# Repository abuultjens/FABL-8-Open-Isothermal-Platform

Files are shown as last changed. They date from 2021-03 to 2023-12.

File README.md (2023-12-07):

# FABL-8-Open-Isothermal-Platform
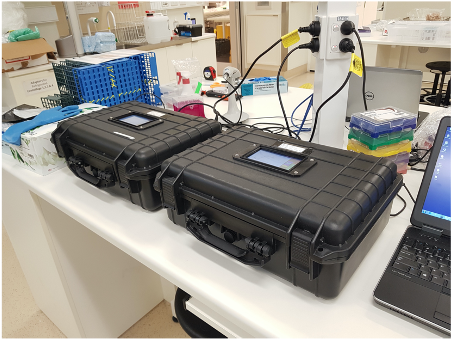
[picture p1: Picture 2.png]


Publicly accessible details on how to build and operate a FABL-8 isothermal diagnostic device. The build instructions have been divided into an essential and optional section. The essential section details how to build just the control, heating, excitation and emission systems as well as a touchscreen interface - the bare minimum for an operating isothermal diagnostic platform. The optional section describes how we built a casing for the instrument, however this specific design was not mandatory for function and could be used as a guide as there is considerable flexibility.

## About
The FABL-8 is an open source, low cost and scalable diagnostic platform for the running and monitoring of loop mediated isothermal amplification (LAMP) reactions. 

## Publication
A research article detailing the FABL-8 and its diagnostic performance against commercial offerings has been published in ACS Biomaterials Science & Engineering (DOI: 10.1021/acsbiomaterials.1c01105):
https://pubs.acs.org/doi/10.1021/acsbiomaterials.1c01105

## Video of instrument in operation
FABL-8 (https://youtu.be/c5SjP3wax4s "FABL-8 isothermal diagnostic platform")

## File download link
https://unimelbcloud-my.sharepoint.com/:f:/r/personal/buultjensa_unimelb_edu_au/Documents/FABL-8_files?csf=1&web=1&e=TzOEO4

## Page index
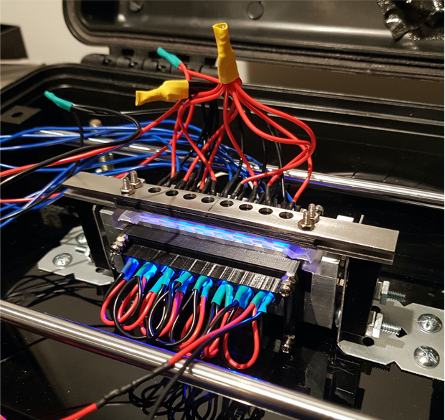
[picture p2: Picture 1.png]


- [Essential build](#essential-build)
  - [Electronic configuration](#electronic-configuration)  
    - [Circuit schematic](#circuit-schematic)
    - [Power source](#power-source)
    - [Setting up the Raspberry pi](#Setting-up-the-Raspberry-pi)
  - [Heating block](#heating-block)
  - [Heating block stands](#heating-block-stands)
  - [3D printed parts](#3d-printed-parts)
    - [Magnet mount](#magnet-mount)
    - [Fixed photodiode mount](#fixed-photodiode-mount)
    - [Fixed LED mount ](#fixed-led-mount)
  - [Assembly](#sssembly)
    - [Block stands and magnet mount](#block-stands-and-magnet-mount)
    - [Excitation system](#excitation-system)
    - [Emission system](#emission-system)
- [Instrument case](#instrument-case)
  - [3D printed parts](#3d-printed-parts)
    - [Left screen mount](#left-screen-mount)
    - [Right screen mount](#right-screen-mount)
    - [Screen face plate](#screen-face-plate)
  - [Block mounting partition](#block-mounting-partition)
- [Instructions of use](#instructions-of-use)
- [Essential build parts list](#essential-build-parts-list)
- [Instrument case parts list](#Instrument-case-parts-list)
- [Script index](#script-index)

# Essential build
This section details how to build just the control, heating, excitation and emission systems as well as a touchscreen interface - the bare minimum for an operating isothermal platform. All required parts can be found in the [Essential build parts list](#essential-build-parts-list).

## Electronic configuration
The circuit consists of five main systems:  
* __Voltage regulation__  
Provide individual step down 5V DC power supplies from the input 19V DC for the control, heater, excitation and emission systems. 
* __Control__  
Consists of a Raspberry pi that orchestrates the heater, excitation and emission systems. The control system uses a 12-stage binary counter to accurately  quantify the clock pulses from the emission system.  
* __Heater__  
Provides high current on/off switching of two 10W wire wound resistors that form the heating element. The heating system utilises a thermal breaker that acts as a failsafe to shutoff the heating element in the event of a control malfunction.
* __Excitation__  
Sequentially illuminates LEDs in an eight LED array using an 8-channel analogue multiplexer.
* __Emission__  
Sequentially reads clock pulses from light-to-frequency photodiodes in an eight photodiode array using an 8-channel analogue demultiplexer.    

Return to [page index](#page-index).

### Circuit schematic  
Note that the thin and thick lines indicate signal wires (current rating: 0.6A) and high current wires (current rating: 7.5A), respectively. 
Image description

Return to [page index](#page-index).

### Power source
We used 19V 6.3A laptop power supply packs as power sources for the FABLE-8 units. Alternatively, a 12V power pack with at least 10A output (120W) would suffice. Using a power supply with a different wattage may cause a different heating profile and the PID parameters may need to be slightly adjusted.

### Setting up the Raspberry pi  

1. Use SDFormatter (https://www.sdcard.org/downloads/) to perform a quick format of a microSD card.  

2. Download the preconfigured image from this page https://cloudstor.aarnet.edu.au/plus/s/Bz4BOmHrPozpWsq.
  
3. Use Raspberry Pi Imager (https://www.raspberrypi.org/software/) to write 'FABL-8_img.img.gz' image to a microSD card.  

Details of all scripts packaged into the image file can be found in the [Script index](#script-index).

Return to [page index](#page-index).

## Heating block
The heating block was made from solid aluminium  using a computer numerical control (CNC) machine. The lid plates and resistor retainer plates were made using a drill press. All 2.5mm holes in the heating block were tapped with metric 3mm (M3) threads.
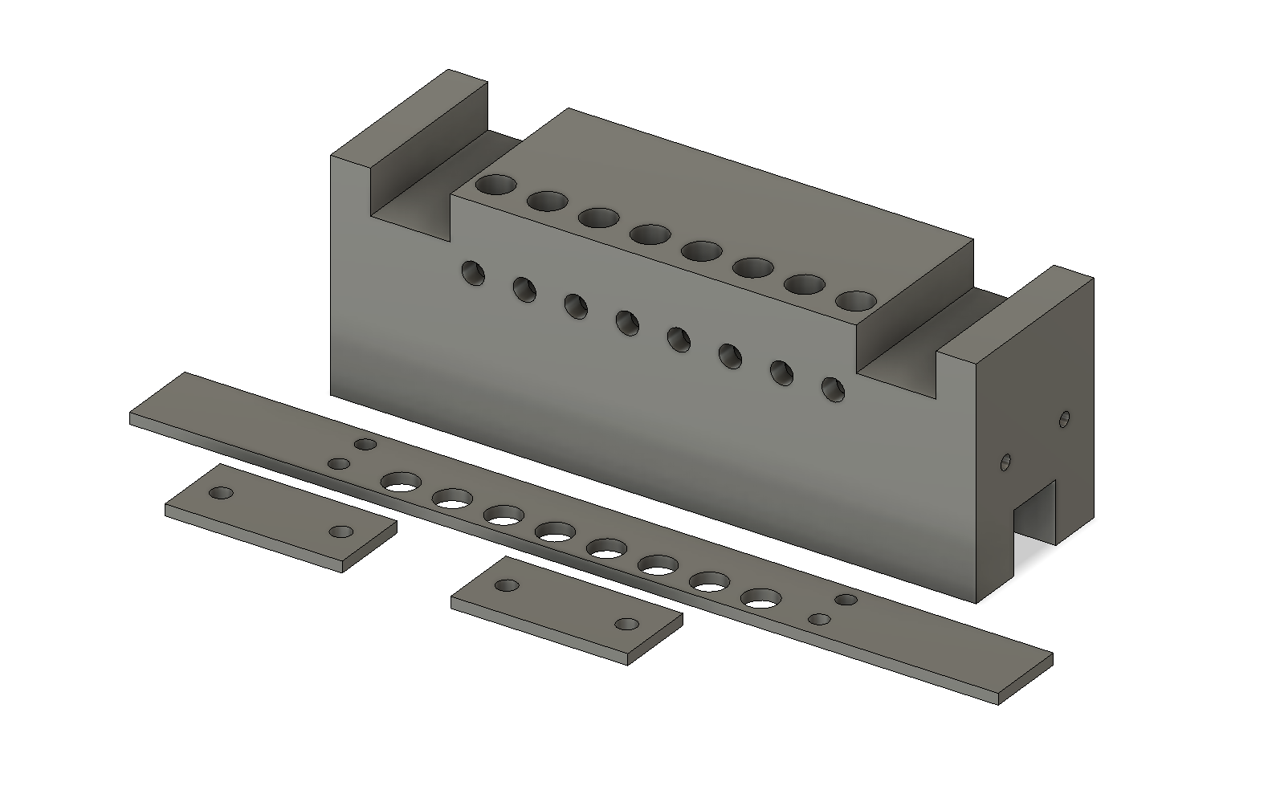
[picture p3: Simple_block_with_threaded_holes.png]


The thermal breaker and temperature sensor are mounted on the rear of the heating block. The thermal breaker mounts using M3 bolts while the temperature sensor is retained using a small clip made from sheet metal that is secured under a thermal breaker mounting bolt head.
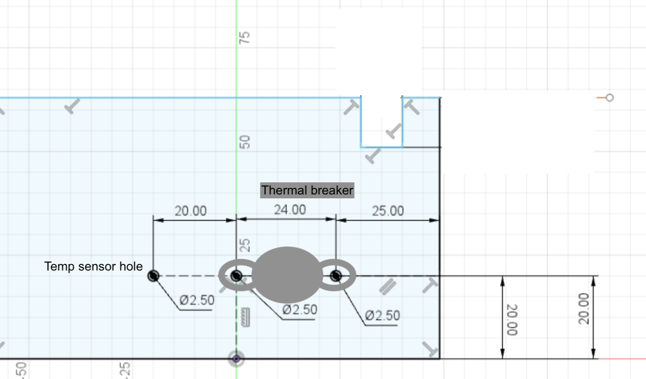
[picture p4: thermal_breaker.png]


Return to [page index](#page-index).

## Heating block stands
Stands were made from 1mm thick sheet metal. If sheet metal is difficult to source or work with, any kind of block mounting stand could be fabricated as long as it can withstand a constant 65oC.
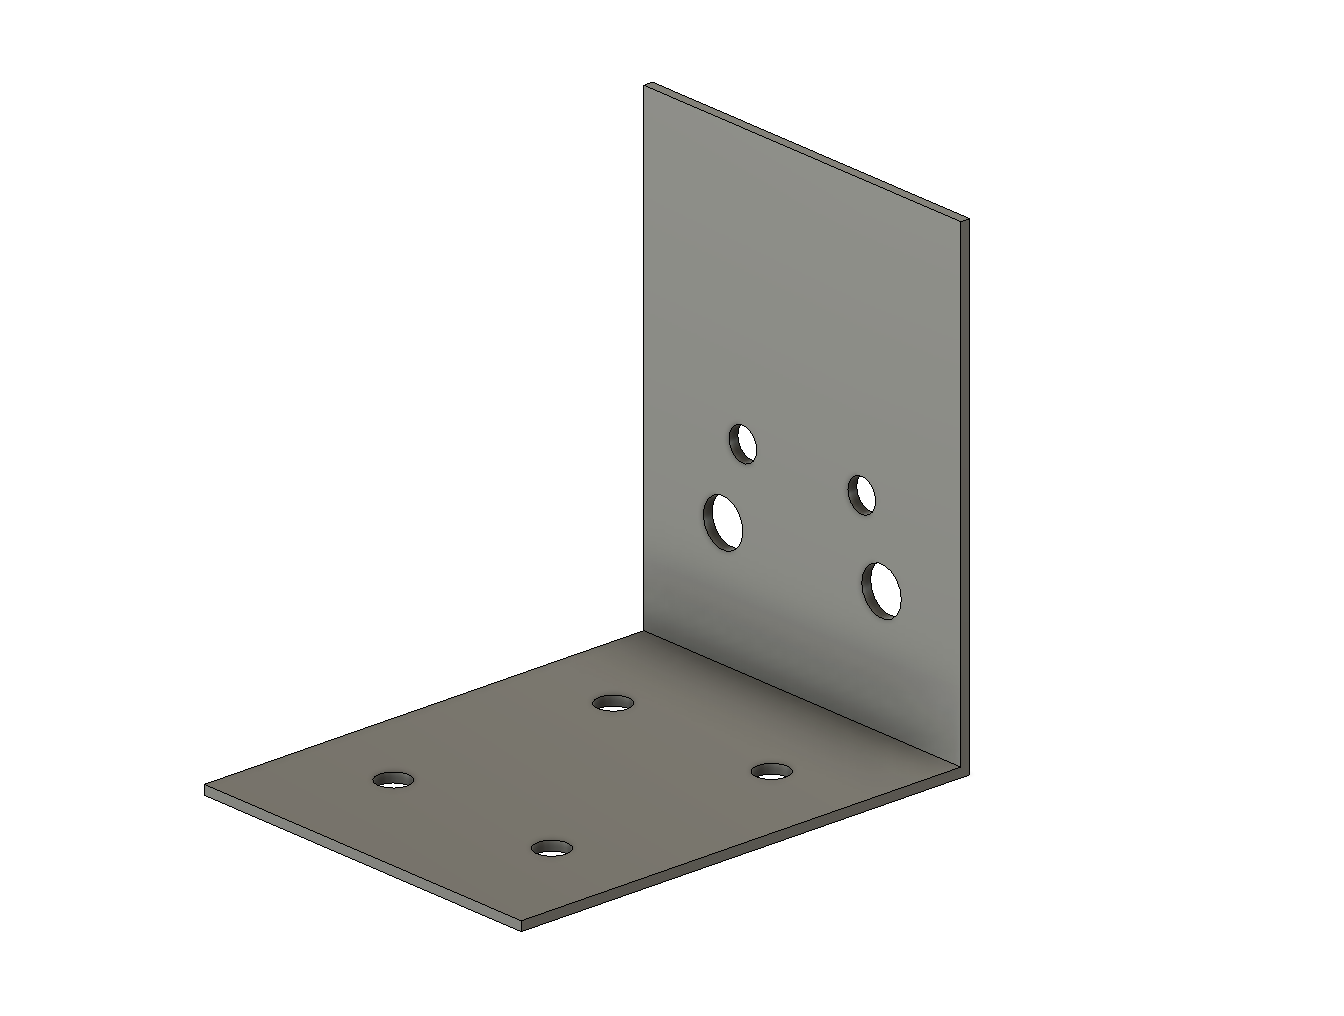
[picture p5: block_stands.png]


Return to [page index](#page-index).

## 3D printed parts
All 3D printed parts were printed using black 1.75 PLA filament on a Creality3D Ender-3 3D printer modified with a BLTouch V2 automatic mechanical bed levelling device (https://www.antclabs.com/bltouch).  

### Magnet mount  
Retains two rare earth magnets in its upper cavity. The mount holds the magnets captive when the closed end of the cavity is facing away from the block.
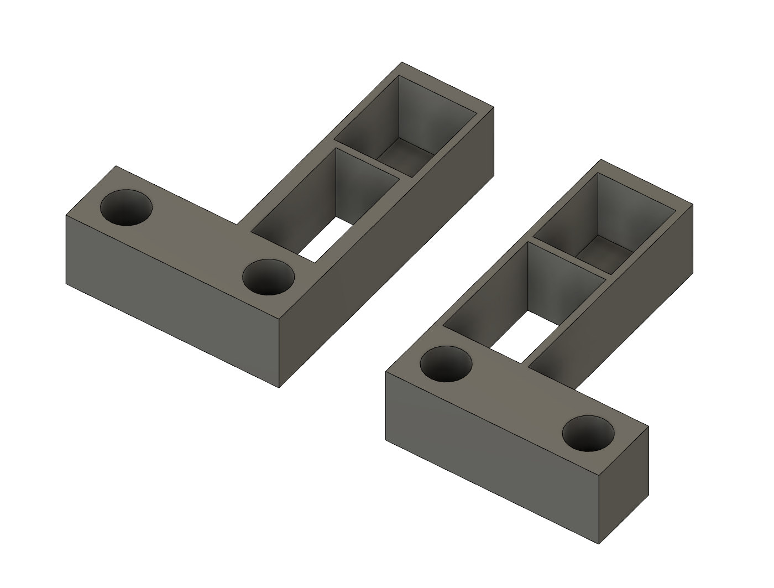
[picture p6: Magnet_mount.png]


Return to [page index](#page-index).

### Fixed photodiode mount  
Retains the eight photodiodes and is sandwiched between two 2mm thick block lid plates. The emission filter gel is mounted between the photodiodes and the lower block lid plate.
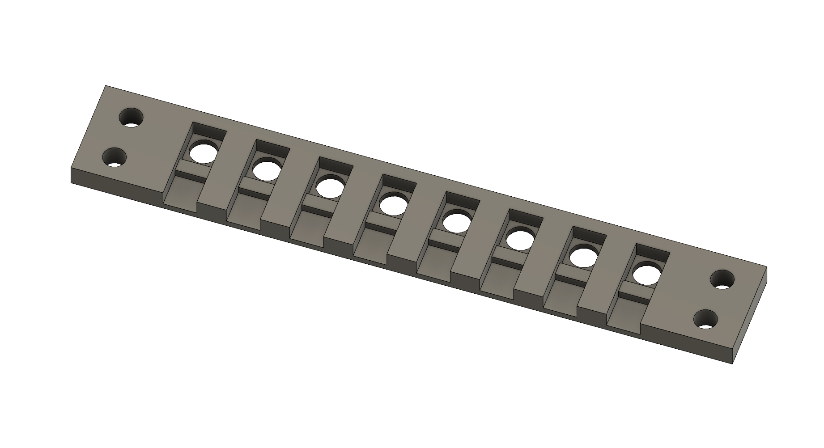
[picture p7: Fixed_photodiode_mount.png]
  

Return to [page index](#page-index).

### Fixed LED mount  
Retains the eight LEDs and clamps the excitation filter gel to the block.
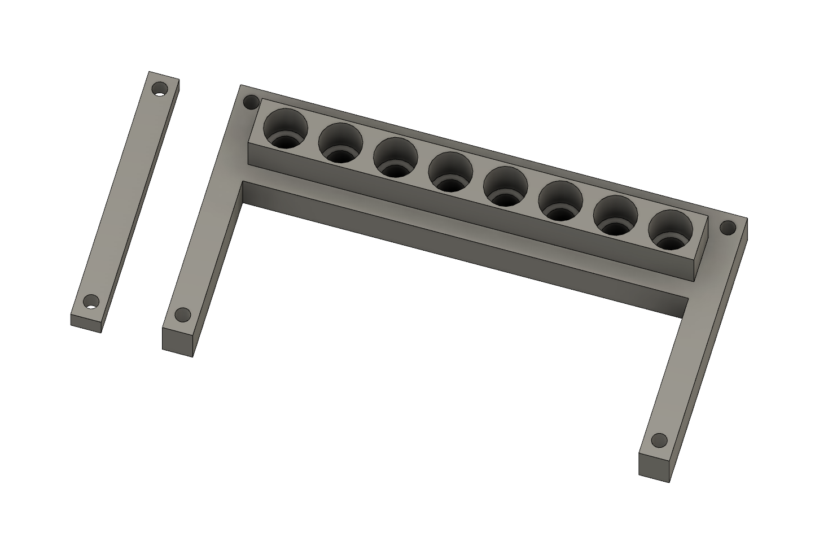
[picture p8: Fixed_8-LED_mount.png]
  

Return to [page index](#page-index).

## Assembly

### Block stands and magnet mount
Two wire wound resistors are fitted into the cavity underneath the heating block and are secured in place using the two resistor retaining plates. The magnet mount is first attached to the block stand with two M5 bolts and nuts. The block is then mounted to the block stand by passing M3 bolts through the gaps in the magnet mounts. 
Image description

Return to [page index](#page-index).

### Excitation system
The eight excitation LEDs are pressed into the fixed LED mount. The excitation gel is sandwiched between the block and the fixed LED mount which is secured in place using M3 bolts, nuts, standoffs and two rear LED mount retainers.
Image description

Return to [page index](#page-index).

### Emission system
The eight photodiodes are fitted into the fixed photodiode mount (with light sensitive surface facing downward through holes) and individually secured with a small piece of sticky tape. The emission filter gels are then overlaid on the light sensitive side of the photodiode mount and secured with the metal lids on both sides using M3 bolts and nuts. Once both block stands are secured to the block, the entire assembly is mounted on a sheet of acrylic.
Image description

Return to [page index](#page-index).

# Instrument case
The key requirements for a FABL-8 casing are firstly that the enclosure blocks out all environmental light and secondly that it provides a thermally insulating environment for the PID controlled heating block to reach and maintain a stable 65oC. Our implementation of the FABL-8 involved a robust briefcase style plastic box and inner acrylic partition that was used to mount the heating block. While this specific setup was ideal for transportation and storage, any casing configuration that meets the abovementioned requirements will suffice. Below we have detailed our case configuration which may be useful as a guide. All required parts can be found in the [Instrument case parts list](#Instrument-case-parts-list).

## 3D printed parts
All 3D printed parts were printed using black 1.75 PLA filament on a Creality3D Ender-3 3D printer modified with a BLTouch V2 automatic mechanical bed levelling device (https://www.antclabs.com/bltouch).  

### Left screen mount  
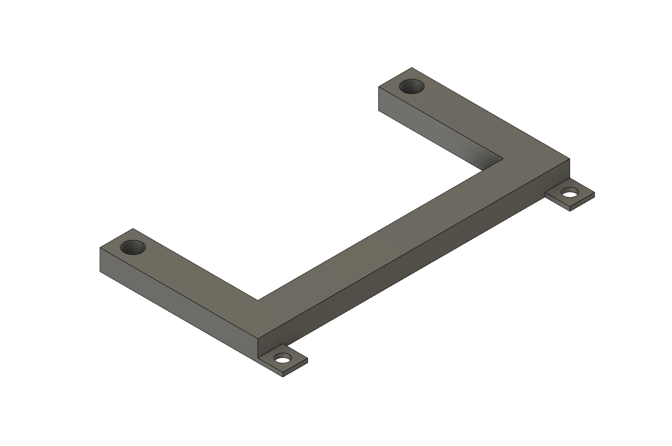
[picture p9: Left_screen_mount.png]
  

Return to [page index](#page-index).

### Right screen mount  
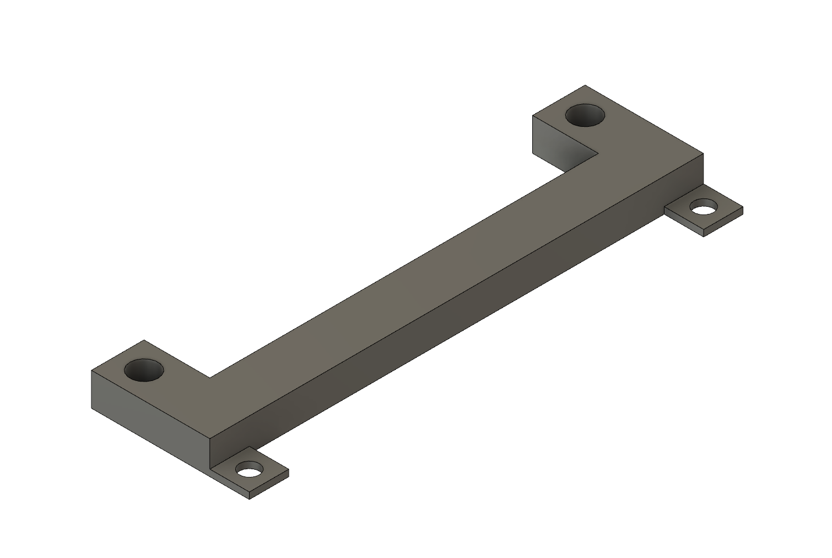
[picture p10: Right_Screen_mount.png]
  

Return to [page index](#page-index).

### Screen face plate  
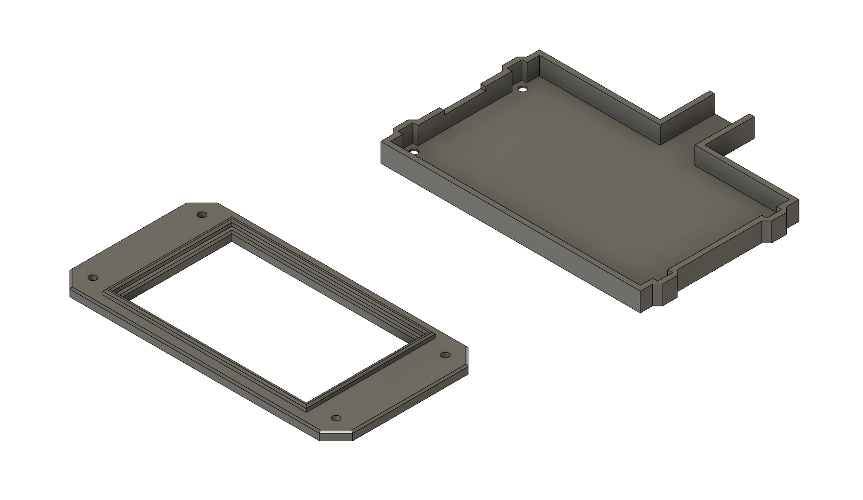
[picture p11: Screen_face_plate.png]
  

Return to [page index](#page-index).

## Block mounting partition
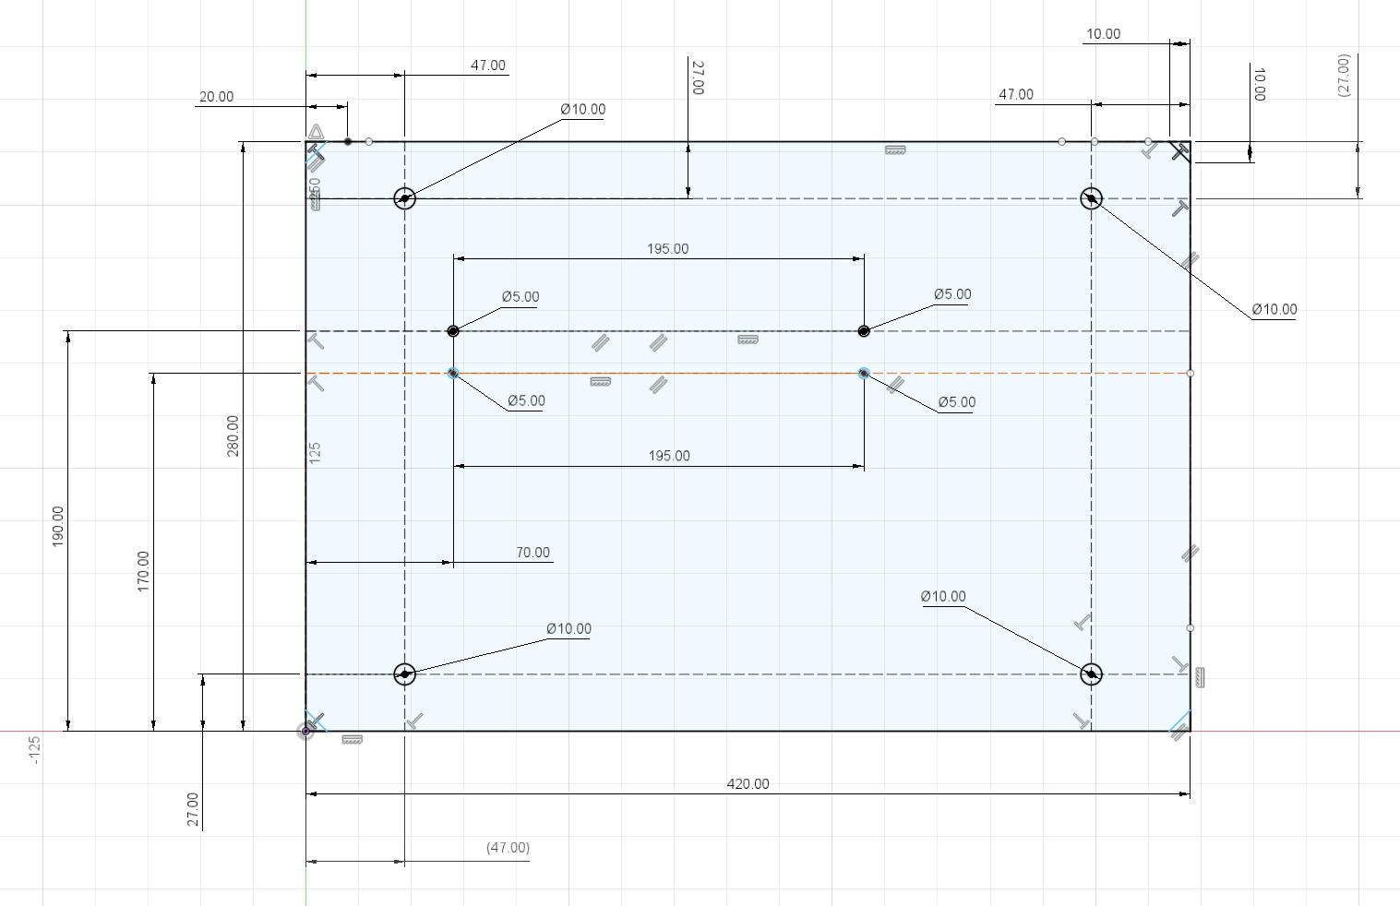
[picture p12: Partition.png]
  

Return to [page index](#page-index).

# Instructions of use  

* An Initial warmup period occurs upon powerup to stably raise the block temperature to 65oC (approximately 10-15 minutes). 

* Instructions for the preparation of the LAMP reactions can be found here: dx.doi.org/10.17504/protocols.io.bqd4ms8w

* Once at operation temperature a reaction can be run by preparing LAMP reagents and template in an OptiGene strip, cutting off the plastic wings on the terminal ends of the strip, removing the magnetic block lid, inserting the strip and replacing the magnetic lid. Specific care must be taken to ensure that all tube lids are firmly pressed closed prior to replacing the block lid.

* The operator then closes the main instrument case lid and uses the touchscreen interface to enter well information and initiate the run. During the run a plot of normalised florescence emission is displayed in real-time. 

* At the conclusion of the run the measurements are saved locally as well as wirelessly uploaded to a webserver via a hotspot hosted by a mobile device. The webserver calculates the derivative of the normalised emission timeseries to classify if the well was positive or negative as well as time to positive (TTP).

Return to [page index](#page-index).

## Essential build parts list
| Part: | Quantity: | Link: |
| --------------- | --------------- | --------------- |
| 12-stage Binary Counter CMOS IC 4040 | 1 | https://www.jaycar.com.au/4040-12-stage-binary-counter-cmos-ic/p/ZC4040 |
| 5M bolts and nuts | 1 | https://www.bunnings.com.au/zenith-m5-x-25mm-316-stainless-steel-round-head-bolt-and-nut-5-pack_p2310748 |
| Arduino Compatible 24V 5A MOS Driver Module | 3 | https://www.auselectronicsdirect.com.au/mos-driver-module-24v-5a-for-arduino-projects?gclid=CjwKCAjwhMmEBhBwEiwAXwFoEZTbsvb9xTaKgrjNCXzyofxZDha0V4Hk5cDGEyZgNib_1PJhzH9eExoCymcQAvD_BwE |
| Arduino Compatible 5V Relay Board | 1 | https://www.jaycar.com.au/arduino-compatible-5v-relay-board/p/XC4419 |
| Arduino Compatible DC Voltage Regulator 2A | 4 | https://www.auselectronicsdirect.com.au/dc-dc-voltage-step-down-converter-module-for-ardui?gclid=Cj0KCQjw3duCBhCAARIsAJeFyPXY0H_Z5v1TH_utRIlQ2Qi64cqLh3KEt3j74XoJ1cvceE0Bd_h9uLgaAl81EALw_wcB |
| Blue 5mm CREE LED 23500mcd Round Clear | 8 | https://www.jaycar.com.au/blue-5mm-cree-led-23500mcd-round-clear/p/ZD0291 |
| DC Power Connector Jack 5 A  2.5 mm  panel mount | 1 | https://au.element14.com/switchcraft-conxall/712a/dc-power-jack-2-5mm-12vdc-5a-solder/dp/1608729 |
| DC power supply 120W 12V | 1 | https://www.jaycar.com.au/12v-dc-10a-desktop-power-supply-2-1mm-dc-plug/p/MP3241 |
| Digital Temperature Sensor Module - DS18B20 | 1 | https://www.jaycar.com.au/digital-temperature-sensor-module/p/XC3700 |
| Emission filter gel: LEE filter 015 and 767 | 1 | http://www.leefilters.com |
| Excitation filter gel: LEE filter 126 | 1 | http://www.leefilters.com |
| HDMI cable 1.5m | 1 | https://www.jaycar.com.au/economy-hdmi-cable-1-5m/p/WV7913?pos=2&queryId=171ab68ba12a5e9c9169ce26e2ab1f60 |
| HDMI resistive touch interface 5inch screen 800x480  | 1 | https://www.jaycar.com.au/5-inch-touchscreen-with-hdmi-and-usb/p/XC9024 |
| Heat Shrink | 1 | https://www.jaycar.com.au/3-0mm-black-heatshrink-tubing/p/WH5532 |
| High current wire (meters) (red and black) | 1 | https://www.jaycar.com.au/black-heavy-duty-hook-up-wire-sold-per-metre/p/WH3041 |
| Low current wire (meters) (various colours) | 2 | https://www.jaycar.com.au/hook-up-wire-pack-2-metres/p/WH3025 |
| M3 bolts 25mm (pack of 25) | 1 | https://www.jaycar.com.au/m3-x-25mm-steel-screws-pk-25/p/HP0414 |
| M3 nuts (pack of 25) | 1 | https://www.jaycar.com.au/m3-steel-nuts-pk-25/p/HP0425 |
| M3 standoff (pack of 8) | 1 | https://www.jaycar.com.au/m3-x-10mm-tapped-metal-spacers-pk8/p/HP0900 |
| M3 washers (pack of 200) | 1 | https://www.jaycar.com.au/3mm-steel-flat-washers-pk-200/p/HP0431 |
| Photodiodes - TSL235R | 8 | https://www.sparkfun.com/products/9768 |
| Phototransistor Optocoupler 4N25/4N28  | 1 | https://www.jaycar.com.au/4n25-4n28-phototransistor-optocoupler/p/ZD1928 |
| Rare Earth Magnets diameter=10mm height=3mm (pack of four) | 1 | https://www.jaycar.com.au/rare-earth-magnet-small-pk-4/p/LM1622 |
| Raspberry Pi 3 Model B+ | 1 | https://au.element14.com/raspberry-pi/raspberry-modb-512m/raspberry-pi-model-b-board/dp/2456986?gclid=CjwKCAjwhMmEBhBwEiwAXwFoEYR2Mwg4QFkwfHrBXNEI6yvINoFfle3anPMrRLCDC8tZpNkloh1qeBoCo4cQAvD_BwE&mckv=_dc%7Cpcrid%7C501152839127%7Cpkw%7C%7Cpmt%7C%7Cslid%7C%7Cproduct%7C2456986%7Cpgrid%7C123988903131%7Cptaid%7Cpla-293946777986%7C&CMP=KNC-GAU-GEN-SMART-SHOPPING |
| Resistor 56 ohm 1/4 Watt | 2 | https://www.jaycar.com.au/56-ohm-1-watt-carbon-film-resistors-pack-of-2/p/RR2544 |
| Single 8-channel Analogue Multiplexer CMOS IC 4051 | 2 | https://www.jaycar.com.au/4051-single-8-channel-analogue-multiplexer-cmos-ic/p/ZC4051 |
| Thermal breaker (80oc) | 1 | https://sinolec.co.uk/en/thermal-cut-out-bimetal-switches/1211447-thermal-cut-out-80c-nc.html |
| Wire Wound Resistor 10 Ohm 10 Watt  | 2 | https://www.jaycar.com.au/10-ohm-10-watt-wire-wound-resistor/p/RR3352 |

Return to [page index](#page-index).

## Instrument case parts list
| Part: | Quantity: | Link: |
| --------------- | --------------- | --------------- |
| Craftright 465 x 360 x 175mm Safe Case | 1 | https://www.bunnings.com.au/craftright-465-x-360-x-175mm-safe-case_p5810252 |
| Black acrylic sheet 6mm thick | 1 | https://www.amazon.com.au/SimbaLux-Acrylic-Plexiglass-Protective-Projects/dp/B07TVKHLP6 |
| IP67 Rated USB Socket - Type A | 1 | https://au.element14.com/multicomp/2ub3001-w05100/sealed-usb-2-0-type-a-receptacle/dp/1850634?gclid=CjwKCAjwhMmEBhBwEiwAXwFoESLVzLMuN3pfnoANTyTBRr4Z1iZKWt3l-58cMxBsgCOkalS_BBS-NxoCSrUQAvD_BwE&mckv=_dc%7Cpcrid%7C501152839127%7Cpkw%7C%7Cpmt%7C%7Cslid%7C%7Cproduct%7C1850634%7Cpgrid%7C123988903131%7Cptaid%7Cpla-293946777986%7C&CMP=KNC-GAU-GEN-SMART-SHOPPING |

Return to [page index](#page-index).

## Script index   
   
### Main scripts   
   
* `APP_v2.py`  
is the main app with interactive menu and live plotting windows

* `PID_SAFE.py`  
orchestrates the PID control of the heating block

* `stepper_SW_colour-sensor_MICROSTEP_CAL.py`  
steps through all eight wells and reads photodiodes  

### Helper scripts
   
* `startup-script.sh`  
script that runs on startup and initiates the app

* `script-replacer.sh`  
this replaces RBP script with newer script(s) from a dir on a remote server  

* `UPDATE-CONFIRM.sh`  
uploads a log file confirming if the updated script(s) have been uploaded to the RBP  

* `MAC_ADDRESS.sh`  
Obtains the Raspberry Pi MAC address and compares it to know addresses to determine which unit the script is running on. This is useful for any specifying any unit/hardware specific parameters when using common scripts. Once the specific hardware has been identified via the MAC address, it make a signal file.

* `PID_SAFE.sh`  
Fetches the set temp and runs PID_SAFE.py  

* `SCP.sh`
SCP outfiles to remote servers and moves run files to local 'SAVE' dir. You will need to insert your own remote server login details in this script. If you don't want to use any remote server(s) then comment out the lines with `sshpass`
  
* `SCP_PID.CSV.sh`
You will need to insert your own remote server login details in this script. If you don't want to use any remote server(s) then comment out the lines with `sshpass`

* `SCP_RUN_DATA.sh`
You will need to insert your own remote server login details in this script. If you don't want to use any remote server(s) then comment out the lines with `sshpass`
  
* `SCP_UPC_CODES.sh`
You will need to insert your own remote server login details in this script. If you don't want to use any remote server(s) then comment out the lines with `sshpass`
  
* `KILL_PID.sh`  
gets PID process ID and kills it  

* `RESTART.sh`  
kills python, sets all GPIO off and restarts app  

* `blink.py`  
sets GPIO pins off  

* `KILL_PYTHON.sh`  
kills python and sets all GPIO off  

Return to [page index](#page-index).

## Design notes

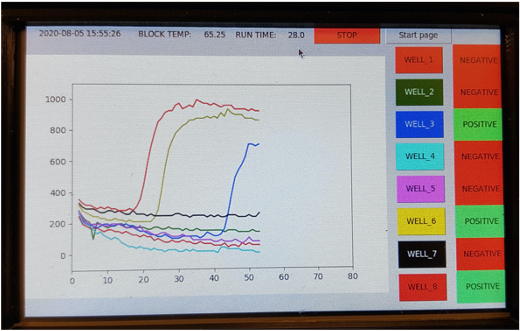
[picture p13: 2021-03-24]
Picture 3.png

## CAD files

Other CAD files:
Simple_block_with_threaded_holes.f3d
